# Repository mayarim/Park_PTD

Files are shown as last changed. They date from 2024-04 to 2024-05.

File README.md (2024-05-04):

# Park_PTD
Cueing device for Parkinson's patients in physical therapy for gait training.
This repository holds the Arduino code for this project. This code was written and tested on the Arduino Nano 33 BLE Rev1 and Rev2.

The main functionality of the code in this repository is to utilize the Arduino Nano 33 BLE's built-in 9-axis IMU to detect steps when worn on or near the ankle and calculate the length of each step taken. If that step is below a given threshold haptic feedback is provided via the vibration disc motor. This provides a cue to patients wearing the device to lengthen their steps.

## Hardware
Integration of the physical components is shown in the following figure:



### (1) Ankle Strap
This can be made using a plastic ring, a length of velcro, and a stapler. First, loop the soft side of the velcro through the ring and stapling to secure it. On the other end secure a smaller length of the hard side of the velcro. The total length should work out to wrap around the ankle without too much overlap.
### (2) Arduino Nano 33 BLE rev1/rev2
The Arduino Nano 33 BLE was chosen for its small form factor while having a 9-axis IMU and BLE module with enough processing power to run any algorithm desired. The Arduino Nano is mounted on a 3D-printed mount (casing_3Dmodels/nano_board_holder_v3.SLDPRT). Screw holes were added to the model, but hot glue works for mounting as well.
### (3) DRV2605L Motor Controller
- DRV2605L Haptic Motor Driver https://www.adafruit.com/product/2305

This motor controller drives the Mini Vibration Motor and provides many preset options in the software to allow customization of the haptic feedback. This is mounted on a 3D-printed mount (casing_3Dmodels/haptic_driver_holdre.SLDPRT). It is fastened using hot glue to the mount. 
The motor driver's VIN, GND, SDA, and SCL pins are wired to the 3.3V, GND, A4, and A5 pins on the Arduino Nano.
### (4) Mini Vibration Disc Motor
- Mini Vibration Disc Motor https://www.adafruit.com/product/1201

Any mini-vibration motor should work as long as it can be driven by the 3.3V output. A longer length of wire between the motor controller and the motor allows the user to place the haptic feedback wherever works best for them. Hot glue is used as strain relief for soldering points.
### (5) 9 Volt Battery. 
A 9-volt battery with a battery clip is used to power the device. A casing was made for the battery (casing_3Dmodels/battery_box_1.SLDPRT) but was further reinforced with duct tape to help reduce movement.
### (6) Switch
This is not shown in the image above, but a toggle switch can be added between the battery and the battery so the device can be easily turned on and off. Hot gluing this to the side of the battery casing ensures minimal movement, and adding hot glue to the soldering point on the switch provides strain relief.

_All CAD files for 3D-printed casing designs are in the **casing_3Dmodels** folder._

## Using the System
Assuming that the correct min_length (or min_len_r2) is uploaded to the device, there is an initial startup sequence for the device. Within this 10-second window, the desired step length can be sent to the device, this period is indicated by an orange light on the Arduino board itself. Once the orange light is off, the device calculates the step length algorithm continuously. If the orange light does not turn off after 10 seconds, the startup sequence likely failed and the system should be powered down and then powered on to try again. When turning on the device a green light should also turn on, this is the power indicator, if there is no green light the system is not on. A reason for the system not being on despite the battery being plugged in is a lack of power in the battery or that the board is broken.

**Note**: The version of the code with the Arduino Nano 33 BLE rev1 should be turned on in an orientation such that the pins on the board are sticking down at the ground. Holding the device up against the underside of a table or flat surface works well. This is for the best performance, not doing so may result in erroneous measurements. This is unnecessary for the rev2.

## Uploading Code
The Arduino Nano 33 BLE can be programmed using a micro-USB connected to a computer running the Arduino IDE https://www.arduino.cc/en/software (or the cloud editor found here https://app.arduino.cc/). This repository can be cloned (functionality should be at the top of the repository) as a ZIP file and opened using the chosen editor. Choose the folder of the desired sketch and click upload. A more in-depth tutorial for the Arduino IDE can be found here https://support.arduino.cc/hc/en-us/articles/4733418441116-Upload-a-sketch-in-Arduino-IDE.

**Note**: When uploading the sketches that have BLE functionality, note that there are lines that should be commented/uncommented specifically for the left and right devices. These lines of code help identify the devices when attempting to connect to the corresponding iOS app. They are labeled with comments in the code near the top of the main sketch file.

## Arduino Sketches
**Note**: The *_r2* version of these Arduino sketches is the version of the sketch for the Arduino Nano 33 BLE Rev2. The sketches without *_r2* at the end are for Rev1. This difference is important as the Rev2 contains a different IMU than the Rev1 and the Rev1 sketches use the Reefwing_LSM9DS1 library to configure the IMU and access the data. The Rev2 sketches use the standard Arduino library Arduino_BMI270_BMM150 to retrieve the IMU values.
### calculate_length / calc_len_r2
This contains code that prints out various values to the connected serial monitor. Its primary use is as a debugger to understand what values are being calculated and to visualize the data being seen. These values include the raw accelerometer, raw gyroscope, normalized acceleration (without gravity), and step calculations. These can be switched between by typing various letters into the serial monitor input such as 'g', 'a', 'n', etc. The full list can be seen in the code.

### send_length / send_len_r2
This code is functionally the same as calculate_length except that code for BLE connection is implemented for testing.

### min_length / min_len_r2
Contains the minimized version of send_length without any reliance on the serial monitor and is the version that should be used when attempting to use the device when relying on battery power. We've found that leaving any statements involving serial output causes the device to not work when not connected to a serial output such as the computer.

### ahrs_visualizer
This is *NOT* an Arduino sketch. It is a Processing (https://processing.org/) sketch and is used to visualize the output of the AHRS to see if the values correctly match the orientation of the device in real life.

## Files
The files in each sketch other than the main file are identical and are helpers to the main file.
### Main File: calculate_length.ino / send_len.ino / min_len.ino
These files are the main sketch files and contain the overall setup and loop logic. The primary calculations for the step length detection and measurement are all implemented in these respective files.
### Filter.h + Filter.cpp
These files define the interface and implement two classes used in the main files: Filter and ZVU.
#### Filter
This class implements a low-pass filter for iterative data based on initialized parameters.
#### ZVU
This outputs a 0 or 1 based on whether there has been significant acceleration activity recently. This was based on the Zero Velocity Update algorithm from https://github.com/Wojtek120/IMU-velocity-and-displacement-measurements/tree/master.
### Integral.h + Integral.cpp
These files define and implement the Integral and DeltaTime classes.
#### Integral
Performs discrete integration using trapezoidal summation. Every input via the step() function is an integration step.
#### DeltaTime
This is a helper class for Integral which helps to calculate the time in seconds between IMU updates. This also converts the measurements from microseconds to seconds.
### Utility.ino
This contains miscellaneous methods that abstract away some repeatedly used code segments. 

## Libraries Used
- https://www.arduino.cc/reference/en/libraries/reefwingahrs/
- https://www.arduino.cc/reference/en/libraries/reefwing_imutypes/
- https://www.arduinolibraries.info/libraries/reefwing-lsm9-ds1
- https://www.arduino.cc/reference/en/libraries/arduinoble/
- https://www.arduino.cc/reference/en/libraries/arduino_bmi270_bmm150/
- https://www.arduino.cc/reference/en/libraries/adafruit-drv2605-library/
- https://www.arduino.cc/reference/en/libraries/vector-datatype/

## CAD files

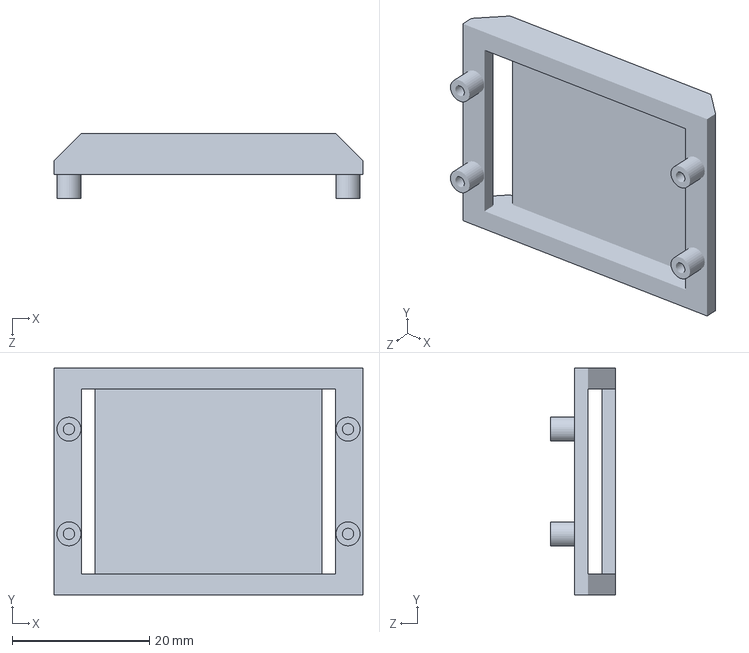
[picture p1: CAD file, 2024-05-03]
casing_3Dmodels/nano_board_holder_v3.SLDPRT
45.0 x 33.0 x 9.50 mm

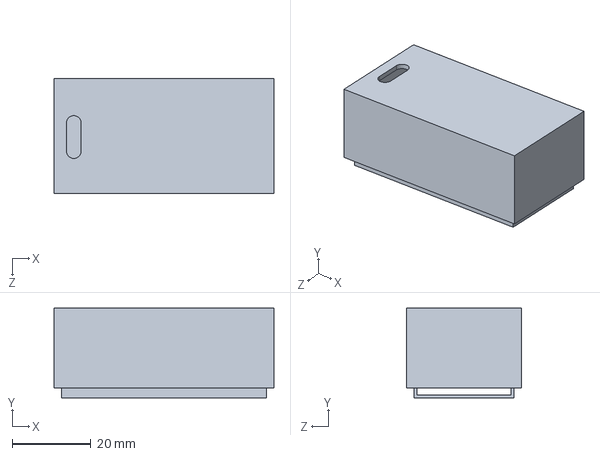
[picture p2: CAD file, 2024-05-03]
casing_3Dmodels/battery_box_1.SLDPRT
55.9 x 22.9 x 29.2 mm

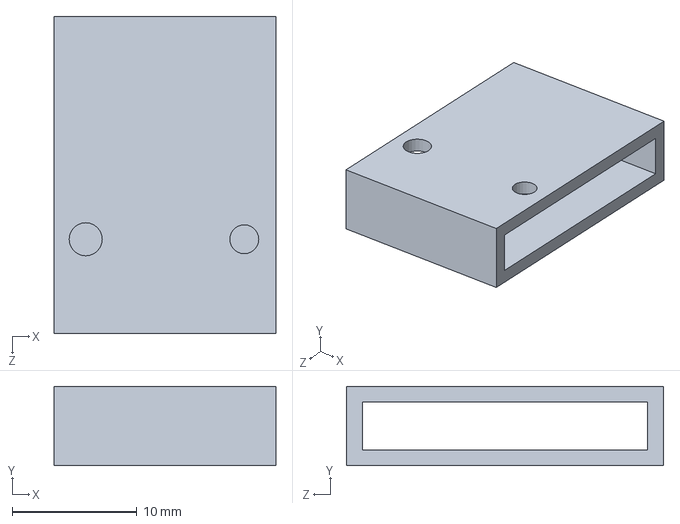
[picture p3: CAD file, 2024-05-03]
casing_3Dmodels/haptic_driver_holdre.SLDPRT
17.8 x 6.35 x 25.4 mm

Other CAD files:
casing_3Dmodels/my_board_holder_attempt.SLDPRT
casing_3Dmodels/battery_box_1.STL
casing_3Dmodels/haptic_driver_holdre.STL

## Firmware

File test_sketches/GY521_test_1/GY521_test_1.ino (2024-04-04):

//
//    FILE: GY521_test_1.ino
//  AUTHOR: Rob Tillaart
// PURPOSE: minimal demo to test working of the sensor.
//     URL: https://github.com/RobTillaart/GY521


#include "GY521.h"

GY521 sensor(0x68);

uint32_t counter = 0;
int POLL_RATE = 200;


void setup()
{
  Serial.begin(115200);
  Serial.println();
  Serial.println(__FILE__);
  Serial.print("GY521_LIB_VERSION: ");
  Serial.println(GY521_LIB_VERSION);

  Wire.begin();

  delay(100);
  while (sensor.wakeup() == false)
  {
    Serial.print(millis());
    Serial.println("\tCould not connect to GY521: please check the GY521 address (0x68/0x69)");
    delay(POLL_RATE);
  }
  sensor.setAccelSensitivity(0);  //  2g
  sensor.setGyroSensitivity(0);   //  250 degrees/s

  sensor.setThrottle();
  Serial.println("start...");
  
  //  set calibration values from calibration sketch.
  sensor.axe = 0;
  sensor.aye = 0;
  sensor.aze = 0;
  sensor.gxe = 0;
  sensor.gye = 0;
  sensor.gze = 0;
}


void loop()
{
  sensor.read();
  float ax = sensor.getAccelZ();
  float ay = sensor.getAccelY();
  float az = sensor.getAccelZ();
  float gx = sensor.getGyroX();
  float gy = sensor.getGyroY();
  float gz = sensor.getGyroZ();
  float t = sensor.getTemperature();

  if (counter % 10 == 0)
  {
    Serial.println("\n\tACCELEROMETER\t\tGYROSCOPE\t\tTEMPERATURE");
    Serial.println("\tax\tay\taz\tgx\tgy\tgz");
  }

//  Serial.print(counter);
//  Serial.print('\t');
  Serial.print(ax, 3);
  Serial.print('\t');
  Serial.print(ay, 3);
  Serial.print('\t');
  Serial.print(az, 3);
  Serial.print('\t');
  Serial.print(gx, 3);
  Serial.print('\t');
  Serial.print(gy, 3);
  Serial.print('\t');
  Serial.print(gz, 3);
//  Serial.print('\t');
//  Serial.print(t, 3);
  Serial.println();

  counter++;
  delay(POLL_RATE);
}


//  -- END OF FILE --

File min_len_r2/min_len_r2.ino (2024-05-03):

#include <ReefwingAHRS.h>
#include <Arduino_BMI270_BMM150.h>
#include <vector_type.h>
#include "Filter.h"
#include "Integral.h"
#include <ArduinoBLE.h>
#include "Adafruit_DRV2605.h"

Adafruit_DRV2605 drv;

// BLE Data Service
BLEService dataService("180A");

// Left Device
BLEStringCharacteristic dataCharacteristic("0000AAAA-0000-1000-8000-00805F9B34FB", BLERead | BLENotify, 128); // 20 is the maximum length of the string
BLEFloatCharacteristic writeCharacteristic("0000BBBB-0000-1000-8000-00805F9B34FB", BLEWrite);

// Right Device
//BLEStringCharacteristic dataCharacteristic("2A57", BLERead | BLENotify, 128);
//BLEFloatCharacteristic writeCharacteristic("6E400002-B5A3-F393-E0A9-E50E24DCCA9E", BLEWrite);

SensorData data;
ReefwingAHRS ahrs;

Filter accelFilter, gyroFilter;
Integral velIntegral, posIntegral;
DeltaTime dt;
ZVU zvu;

#define GRAVITY 9.81
#define ACCEL_THRESH 1
#define GYRO_THRESH 3.0
#define MIN_STEP_LENGTH 0.02
#define MAX_STEP_LENGTH 5.00
#define M_TO_CM 100

char input = 'F';

float step_cum = 0;
float step_target = 0.50;

bool connectBLE = true;

void setup() {
  pinMode(LED_BUILTIN, OUTPUT);
  digitalWrite(LED_BUILTIN, HIGH); // turn on the built-in LED
  
  ahrs.begin();

  accelFilter.begin(5, 119); 
  gyroFilter.begin(5, 119);
  zvu.begin(ACCEL_THRESH, GYRO_THRESH, 12);
  
  ahrs.setFusionAlgorithm(SensorFusion::MAHONY);
  ahrs.setDeclination(-9.25059);
  ahrs.setKp(40.0);
  ahrs.setKi(0.0);
//  ahrs.setBeta(0);
//  ahrs.setAlpha(0.95);
 // Serial.begin(115200);
//  while (!Serial);

  // Init Motor Driver
  while(!drv.begin()) {
    delay(10);
  }
  
  drv.setMode(DRV2605_MODE_INTTRIG); // default, internal trigger when sending GO command
  drv.selectLibrary(1);
  drv.setWaveform(0, 84);  // ramp up medium 1, see datasheet part 11.2
  drv.setWaveform(1, 1);  // strong click 100%, see datasheet part 11.2
  drv.setWaveform(2, 0);  // end of waveforms

  // Init BLE
  while(!BLE.begin()){
    delay(10);
  }
//  BLE.setLocalName("Right Step Detector");
  BLE.setLocalName("Left Step Detector");
  BLE.setAdvertisedService(dataService);
  BLE.setAdvertisingInterval(100);

  // add the characteristics to the service
  dataService.addCharacteristic(dataCharacteristic);
  dataService.addCharacteristic(writeCharacteristic);

  // add service
  BLE.addService(dataService);

  // start advertising
  BLE.advertise();
 //   Serial.println("BLE Started.");

  // Init IMU
  while(!IMU.begin()){
    delay(10);
  }

//  Serial.println("Ready!!!\n");

  while(1) {
//    if(Serial.available()){
//      input = readChar();
//    }
//    BLEDevice central;
////    central = BLE.central();
//    if(connectBLE) bleFetch();
    updateLoop();
  }
  
}

void minUpdate(){
  if (IMU.gyroscopeAvailable()) {  
    IMU.readGyroscope(data.gx, data.gy, data.gz);
    data.gTimeStamp = micros();
  }
  if (IMU.accelerationAvailable()) {  
    IMU.readAcceleration(data.ax, data.ay, data.az);  
    data.aTimeStamp = micros();
  }
  if (IMU.magneticFieldAvailable()) {
    IMU.readMagneticField(data.mx, data.my, data.mz);
    data.mTimeStamp = micros();
  }
  ahrs.setData(data); //data is a struct {ax,ay,az,gx,gy,gz,mx,my,mz,gTimeStamp,aTimeStamp,mTimeStamp}
  ahrs.update();
}

void updateLoop(){
  minUpdate();
  vec3_t accel = getAccel(data);
  vec3_t gyro = getGyro(data);
  vec3_t accel_filtered = accelFilter.step(accel);
  vec3_t gyro_filtered = gyroFilter.step(gyro);
  vec3_t gravity = getGravity(ahrs.getQuaternion());
  vec3_t ag = projectAccelOnGravity(accel, gravity) * GRAVITY * 2 ;
  bool notMoving = zvu.check(ag, gyro);
  switch(input){
//    case 'G':
//      printVector("Gyro: ", gyro);
//      break;
//    case 'N':
//      printVector("Proj_Norm: ", ag, ACCEL_THRESH * notMoving);
//      break;
    case 'S': {
      if(notMoving){
        float len = posIntegral.cum.mag();
        if(len > MIN_STEP_LENGTH && len < MAX_STEP_LENGTH) {
//          printVector("Position: ", posIntegral.cum);
          step_cum += len;
    //      Serial.print("Cumulative dist: ");
     //     Serial.print(step_cum);
      //    Serial.print(" Total Time: ");
     //     Serial.print(dt.cumDiff(data.aTimeStamp));
      //    Serial.print(" Timestamp: ");
      //    Serial.println(data.aTimeStamp); // Tommy wants output: time,step_length
          if(len < step_target){
            vibrate();
          }
          if(connectBLE) bleSend(buildDataString(data.aTimeStamp, len));
        }
        resetPos();
        dt.first = data.aTimeStamp;
      }
      else calculatePos(ag, data.aTimeStamp);
      break;
    }
    case 'C':
      step_cum = 0;
      input = 'S';
      break;
    case 'F':{
      unsigned long start = millis();
//      Serial.println("Fetching Step Length...");
      while(1){
        unsigned long diff = millis() - start;
        if(diff >= 10000){
          break;
        }
//        if(diff % 1000 < 5) {
////          Serial.print(diff / 1000);
////          Serial.println("...");
//        }
        minUpdate();
        bleFetch();
      }
      digitalWrite(LED_BUILTIN, LOW);

      input = 'C';
      break;
    }
    default:
      break;
  }
}

vec3_t getGravity(Quaternion q){
  float r0 = 2*(q.q1*q.q3-q.q0*q.q2);
  float r1 = 2*(q.q2*q.q3+q.q0*q.q1);
//  float r2 = 2*(q.q0*q.q0+q.q3*q.q3)-1;
  float r2 = q.q0*q.q0 - q.q1*q.q1 - q.q2*q.q2 + q.q3*q.q3;
  return {r0, r1, r2};
}

vec3_t projectAccelOnGravity(vec3_t a, vec3_t g){
  return a - a.dot(g)*g;
}

vec3_t subtractGravity(vec3_t a, vec3_t g){
  return a - g;
}

vec3_t calculatePos(vec3_t a, uint32_t ts){
  float delta = dt.step(data.aTimeStamp);
  return posIntegral.step(velIntegral.step(a, delta), delta);
}

void resetPos(){
  velIntegral.reset(getAccel(data));
  posIntegral.reset({0, 0, 0});
  dt.set(data.aTimeStamp);
}

void resetVelocity() {
  velIntegral.reset(getAccel(data));
  posIntegral.resetPrev({0, 0, 0});
  dt.set(data.aTimeStamp);
}

void vibrate(){
  drv.go();
}

void loop() {}

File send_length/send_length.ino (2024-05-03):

#include <ReefwingAHRS.h>
#include <ReefwingLSM9DS1.h>
#include <vector_type.h>
#include "Filter.h"
#include "Integral.h"
#include <ArduinoBLE.h>

// BLE Data Service
BLEService dataService("180A");

// BLE Data Characteristic - custom 128-bit UUID, read and notify
BLEStringCharacteristic dataCharacteristic("0000AAAA-0000-1000-8000-00805F9B34FB", BLERead | BLENotify, 128); // 20 is the maximum length of the string

// New characteristic to be written to by external devices
//BLEByteCharacteristic writeCharacteristic("0000BBBB-0000-1000-8000-00805F9B34FB", BLEWrite);
BLEFloatCharacteristic writeCharacteristic("0000BBBB-0000-1000-8000-00805F9B34FB", BLEWrite);

ReefwingLSM9DS1 imu;
ReefwingAHRS ahrs;
//Configuration imuConfig;

Filter accelFilter, gyroFilter;
Integral velIntegral, posIntegral;
DeltaTime dt;
ZVU zvu;

#define GRAVITY 9.81
#define ACCEL_THRESH 1
#define GYRO_THRESH 3.0

char input = 'G';

float step_cum = 0;
float step_target = 0;

bool connectBLE = false;

void setup() {
  imu.begin();
  ahrs.begin();

  accelFilter.begin(5, 119);
  gyroFilter.begin(5, 119);
  zvu.begin(ACCEL_THRESH, GYRO_THRESH, 30);
  
  ahrs.setFusionAlgorithm(SensorFusion::MAHONY);
  ahrs.setDeclination(-9.25059);
  ahrs.setKp(40.0);
  ahrs.setKi(0.0);
//  ahrs.setBeta(0);
//  ahrs.setAlpha(0.95);
  Serial.begin(115200);
  while (!Serial);

  // Init BLE
  if (!BLE.begin()) {
    Serial.println("BLE initialization failed!!!");
    while (1);
  } else {
    BLE.setLocalName("NanoParkinsons");
    BLE.setAdvertisedService(dataService);
    BLE.setAdvertisingInterval(100);
  
    // add the characteristics to the service
    dataService.addCharacteristic(dataCharacteristic);
    dataService.addCharacteristic(writeCharacteristic);
  
    // add service
    BLE.addService(dataService);
  
    // start advertising
    BLE.advertise();
    Serial.println("BLE Started.");
  }

  // Init IMU
  if (imu.connected()) {
    imu.setGyroODR(GODR_952Hz);
    Serial.println("LSM9DS1 IMU Connected."); 
    Serial.println("Calibrating IMU...\n"); 
    imu.start();
    imu.calibrateGyro();
    imu.calibrateAccel();
    imu.calibrateMag();

    delay(20);
    //  Flush the first reading - this is important!
    //  Particularly after changing the imuConfiguration.
    imu.readGyro();
    imu.readAccel();
    imu.readMag();


/***********************
 * DON'T USE imu.getConfig()
 * For some reason causes gyro to have non-zero readings when device is not moving
 */
//    imuConfig = imu.getConfig(); 
//    printConfig();

//    imu.updateSensorData();
//    resetIntegrals();
  } 
  else {
    Serial.println("LSM9DS1 IMU Not Detected.");
    while(1);
  }

  Serial.println("Ready!!!\n");

  while(1) {
    if(Serial.available()){
      input = readChar();
    }
//    BLEDevice central;
////    central = BLE.central();
//    if(connectBLE) bleFetch();
    updateLoop();
  }
  
}

void updateLoop(){
  imu.updateSensorData();
  ahrs.setData(imu.data); //imu.data is a struct {ax,ay,az,gx,gy,gz,mx,my,mz,gTimeStamp,aTimeStamp,mTimeStamp}
  ahrs.update();
  vec3_t accel = getAccel(imu.data);
  vec3_t gyro = getGyro(imu.data);
  vec3_t accel_filtered = accelFilter.step(accel);
  vec3_t gyro_filtered = gyroFilter.step(gyro);
  vec3_t gravity = getGravity(ahrs.getQuaternion());
  vec3_t ag = projectAccelOnGravity(accel, gravity) * GRAVITY * 2 ;
  bool notMoving = zvu.check(ag, gyro);
  switch(input){
    case 'G':
      printVector("Gyro: ", gyro);
      break;
    case 'H':
      printVector("Gyro_filtered: ", gyro_filtered);
      break;
    case 'A':
      printVector("Accel: ", accel);
      break;
    case 'B':
      printVector("Accel_filtered: ", accel_filtered);
      break;
    case 'N':
      printVector("Proj_Norm: ", ag, ACCEL_THRESH * notMoving);
      break;
    case 'P': {
      calculatePos(ag, imu.data.aTimeStamp);
      printVector("AVP: ", velIntegral.prev.mag(), velIntegral.cum.mag(), posIntegral.cum.mag());
      break;
    }
    case 'R': {
      resetPos();
      input = 'P';
      break;
    }
    case 'S': {
      if(notMoving){
        if(posIntegral.cum.mag() > 0.02) {
          printVector("Position: ", posIntegral.cum);
          float len = posIntegral.cum.mag();
          step_cum += len;
          Serial.print("Cumulative dist: ");
          Serial.print(step_cum);
          Serial.print(" Total Time: ");
          Serial.print(dt.cumDiff(imu.data.aTimeStamp));
          Serial.print(" Timestamp: ");
          Serial.println(imu.data.aTimeStamp); // Tommy wants output: time,step_length
          if(connectBLE) bleSend(buildDataString(imu.data.aTimeStamp, len));
        }
        resetPos();
        dt.first = imu.data.aTimeStamp;
      }
      else calculatePos(ag, imu.data.aTimeStamp);
      break;
    }
    case 'C':
      step_cum = 0;
      input = 'S';
      break;
//    case 'Q':
//      vec3_t ag = projectAccelOnGravity(accel_filtered, gravity);
//      calculatePos(ag, imu.data.aTimeStamp);
//      printVector("AVP: ", velIntegral.prev.x, velIntegral.cum.x, posIntegral.cum.x);
//      break;
//    case 'S':
//      velIntegral.reset(accel, imu.data.aTimeStamp);
//      posIntegral.reset({0, 0, 0}, imu.data.aTimeStamp);
//      input = 'Q';
//      break;
    case 'Z': {
      connectBLE = !connectBLE;
      Serial.print("connectBLE = ");
      Serial.println(connectBLE);
      input = 'F';
      break;
    }
    case 'F':
      if(connectBLE) bleFetch();
      break;
    default:
      break;
  }
}

vec3_t getGravity(Quaternion q){
  float r0 = 2*(q.q1*q.q3-q.q0*q.q2);
  float r1 = 2*(q.q2*q.q3+q.q0*q.q1);
//  float r2 = 2*(q.q0*q.q0+q.q3*q.q3)-1;
  float r2 = q.q0*q.q0 - q.q1*q.q1 - q.q2*q.q2 + q.q3*q.q3;
  return {r0, r1, r2};
}

vec3_t projectAccelOnGravity(vec3_t a, vec3_t g){
  return a - a.dot(g)*g;
}

vec3_t subtractGravity(vec3_t a, vec3_t g){
  return a - g;
}

vec3_t calculatePos(vec3_t a, uint32_t ts){
  float delta = dt.step(imu.data.aTimeStamp);
//  Serial.print("dt: ");
//  Serial.println(delta, 6);
  return posIntegral.step(velIntegral.step(a, delta), delta);
}

void resetPos(){
  velIntegral.reset(getAccel(imu.data));
  posIntegral.reset({0, 0, 0});
  dt.set(imu.data.aTimeStamp);
}

void resetVelocity() {
  velIntegral.reset(getAccel(imu.data));
  posIntegral.resetPrev({0, 0, 0});
  dt.set(imu.data.aTimeStamp);
}

void loop() {}

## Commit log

2024-05-03 control flow works, poor accuracy
2024-05-03 minimal length calculation code for battery power
2024-05-03 code for rev2 (r2) working, sample rate much lower though
2024-05-03 CAD files for casing pieces - to main
    [battery_box_1.SLDPRT, battery_box_1.STL, haptic_driver_holdre.SLDPRT, haptic_driver_holdre.STL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]
